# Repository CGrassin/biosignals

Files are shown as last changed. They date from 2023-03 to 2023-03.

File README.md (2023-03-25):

# BioSignals

**This project is work-in-progress.**

BioSignals is a multi-channel, up to 24-bits resolution acquisition system for bio-potentials (EMG, ECG, EEG and more). 

Repository structure:
* **Firmware_BioSignals**: the firmware to be programmed on the board with STM32duino.
* **Electronics_BioSignals**: the circuit board files.
* **Software_BioSignals**: software for the host computer
* **CAD_BioSignals**: 3D files (EEG headware).
* **Interface.md**: description of the data and command interface to the board.

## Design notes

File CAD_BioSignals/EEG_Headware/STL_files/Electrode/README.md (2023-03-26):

# Electrodes holders

Forked from the Ultracortex "Mark III Nova REVISED" repository: https://github.com/OpenBCI/Ultracortex/tree/master/Mark_III_Nova_REVISED

## Print Settings

* Material: PLA
* Supports: NO
* Raft: NO
* Infill: 20%
* Layer Height: 0.2mm
* Number of Shells: 3
* Speed while extruding: 50-70% (slow it down if possible; these parts are detailed)

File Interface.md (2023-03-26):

# Data and command interface

Forked from https://github.com/OpenBCI/Documentation

## Data format

BioSignals sends 33 bytes long packets, following the OpenBCI Cyton data output format.

Each packet contains a header followed by a sample counter, followed by 8 ADS channel data, followed by the three axes values of the accelerometer, followed by a footer. The accelerometer data are optional, and don't need to be sent with every packet when used. if unused, the bytes will read 0. This allows for user defined auxiliary data to be sent in the last six bytes before the footer. Also, there may be room for compressing more samples. Here are details on the format.

**Header**

-   Byte 1: 0xA0  
-   Byte 2: Sample Number

**EEG Data**  
Note: values are 24-bit signed, MSB first

-   Bytes 3-5: Data value for EEG channel 1  
-   Bytes 6-8: Data value for EEG channel 2  
-   Bytes 9-11: Data value for EEG channel 3  
-   Bytes 12-14: Data value for EEG channel 4  
-   Bytes 15-17: Data value for EEG channel 5  
-   Bytes 18-20: Data value for EEG channel 6  
-   Bytes 21-23: Data value for EEG channel 6  
-   Bytes 24-26: Data value for EEG channel 8  

**Aux Data**

-   Bytes 27-32: 6 bytes of data defined and parsed based on the **Footer** below

**Footer**  

-   Byte 33: 0xCX where X is 0-F in hex

The following table is sorted by `Stop Byte`. Drivers should use the `Stop Byte` to determine how to parse the 6 `AUX` bytes.

| Byte 27 | Byte 28 | Byte 29 | Byte 30 | Byte 31 | Byte 32 | Stop Byte | Name                                |
| :-----: | :-----: | :-----: | :-----: | :-----: | :-----: | :-------: | ----------------------------------- |
|   AX1   |   AX0   |   AY1   |   AY0   |   AZ1   |   AZ0   |    0xC0   | Standard with accel                 |
|   UDF   |   UDF   |   UDF   |   UDF   |   UDF   |   UDF   |    0xC1   | Standard with raw aux               |
|   UDF   |   UDF   |   UDF   |   UDF   |   UDF   |   UDF   |    0xC2   | User defined                        |
|    AC   |    AV   |    T3   |    T2   |    T1   |    T0   |    0xC3   | Time stamped **_set_** with accel   |
|    AC   |    AV   |    T3   |    T2   |    T1   |    T0   |    0xC4   | Time stamped with accel             |
|   UDF   |   UDF   |    T3   |    T2   |    T1   |    T0   |    0xC5   | Time stamped **_set_** with raw aux |
|   UDF   |   UDF   |    T3   |    T2   |    T1   |    T0   |    0xC6   | Time stamped with raw aux           |

### 24-Bit Signed Data Values conversion

For the EEG data values, you will note that we are transferring the data as a 24-bit signed integer, which is a bit unusual. We are using this number format because it is the native format used by the ADS129x chip that is at the core of the BioSignals board. To convert this unusual number format into a more standard 32-bit signed integer, you can use the following snippet (Java):

```java

int interpret24bitAsInt32(byte[] byteArray) {     
    int newInt = (  
     ((0xFF & byteArray[0]) <! 16) |  
     ((0xFF & byteArray[1]) <! 8) |   
     (0xFF & byteArray[2])  
    );  
    if ((newInt & 0x00800000) > 0) {  
      newInt |= 0xFF000000;  
    } else {  
      newInt &= 0x00FFFFFF;  
    }  
    return newInt;  
}  

```

## Command interface

On startup, the board sends the following text over the radio:

```

OpenBCI V3 8-16 channel
ADS1299 Device ID: 0xXX
LIS3DH Device ID: 0xXX
Firmware: vX.X.X
$$$

```

### Turn Channels OFF

**1 2 3 4 5 6 7 8**  
These ASCII characters turn the respective channels [1-8] off. The channel will read 0.00 when off during streamData mode. These commands work in and out of streamData mode.

**returns** none, there is no confirmation.

### Turn Channels ON

**! @ # $ % ^ &  \***  
These ASCII characters turn the respective channels [1-8] on. The channel will read ADC output values during streamData mode. These commands work in and out of streamData mode.

**returns** none, there is no confirmation.

### Test Signal Control Commands

**0 - = p [ ]**  
Turn **all** available channels on, and connect them to internal test signal. These are useful for self test and calibration. For example, you can measure the internal noise by sending **0** which connects all inputs to an internal GND. If streaming, the stream will be stopped, the proper registers set on the ADS1x9x, and the stream will be resumed.

-   **0**  Connect to internal GND (VDD - VSS)  
-   **-**  Connect to test signal 1xAmplitude, slow pulse  
-   **=**  Connect to test signal 1xAmplitude, fast pulse  
-   **p**  Connect to DC signal  
-   **\[**  Connect to test signal 2xAmplitude, slow pulse  
-   **]**  Connect to test signal 2xAmplitude, fast pulse  

**Note: Not all possible internal test connections are implemented here.**

**returns** If not streaming, returns `Success: Configured internal test signal.$$$`, if streaming, there is no confirmation.

### Channel Setting Commands

** x (CHANNEL, POWER_DOWN, GAIN_SET, INPUT_TYPE_SET, BIAS_SET, SRB2_SET, SRB1_SET) X **  
Channel Settings commands have six parameters for each ADS channel. To access Channel Settings, first send **x**. The OpenBCI board will then expect the next 7 bytes to be channel settings specific commands. The first byte is the channel number. (If you have the Daisy Module, you can select up to 16 channels to set). The following six ASCII characters are accepted as parameters to set. Lastly, sending **X** will latch the settings to the ADS channel.

**CHANNEL**

-   **1 2 3 4 5 6 7 8**  for single board channel select
-   **Q W E R T Y U I**  for selecting channels on the Daisy Module

**POWER_DOWN**

-   0 = ON (default)
-   1 = OFF    

**GAIN_SET**

-   0 = Gain 1
-   1 = Gain 2
-   2 = Gain 4
-   3 = Gain 6
-   4 = Gain 8
-   5 = Gain 12
-   6 = Gain 24	(default)

**INPUT_TYPE_SET**  
Select the ADC channel input source  

-   0        ADSINPUT_NORMAL     	(default)  
-   1        ADSINPUT_SHORTED          
-   2        ADSINPUT_BIAS_MEAS  
-   3        ADSINPUT_MVDD  
-   4        ADSINPUT_TEMP  
-   5        ADSINPUT_TESTSIG  
-   6        ADSINPUT_BIAS_DRP  
-   7        ADSINPUT_BIAS_DRN  

**BIAS_SET**  
Select to include the channel input in BIAS generation.

-   0 = Remove form BIAS
-   1 = Include in BIAS  (default)  

**SRB2_SET**  
Select to connect this channel's P input to the SRB2 pin. This closes a switch between P input and SRB2 for the given channel, and allows the P input also remain connected to the ADC.  

-   0 = Disconnect this input from SRB2
-   1 = Connect this input to SRB2  (default)  

**SRB1_SET**  
Select to connect all channels' N inputs to SRB1. This effects all pins, and disconnects all N inputs from the ADC.  

-   0 = Disconnect all N inputs from SRB1 (default)
-   1 = Connect all N inputs to SRB1  

**EXAMPLE**

User sends **x  3  0  2  0  0  0  0  X**

'x' enters Channel Settings mode. Channel 3 is set up to be powered up, with gain of 2, normal input, removed from BIAS generation, removed from SRB2, removed from SRB1. The final 'X' latches the settings to the ADS1x9x channel settings register.

You may stack multiple channel settings together such as:

**EXAMPLE**

User sends **x1020000Xx2020000Xx3020000X**

This will set the first three channels.

**returns**

On success:

-   If streaming, no confirmation of success. Note: WiFi Shields will always get a response, even if streaming.
-   If not streaming, returns `Success: Channel set for 3$$$`, where 3 is the channel that was requested to be set.

On failure:

-   If not streaming, NOTE: WiFi shield always sends the following responses without `$$$`
    -   Not enough characters received, `Failure: too few chars$$$` (**example** user sends x102000X)
    -   9th character is not the upper case 'X', `Failure: 9th char not X$$$` (**example** user sends x1020000V)
    -   Too many characters or some other issue, `Failure: Err: too many chars$$$`
-   If not all commands are not received within 1 second, `Timeout processing multi byte message - please send all commands at once as of v2$$$`

**Note: 24&times; gain, SRB1_SET and SRB2_SET are only supported by the ADS1299.**

### Default Channel Settings

**d** To set all channels to default  

**returns** if not streaming, `updating channel settings to default$$$`

**D** To get a report of the default settings send.

**returns** When you query the default settings, expect to get 6 ASCII characters followed by **$$$**

<!-- _Note: Users can change the default channel settings in the initialization function inside the OpenBCI library. Requires re-programming the board._ -->

### LeadOff Impedance Commands

**z (CHANNEL, PCHAN, NCHAN) Z**  
This works similar to the Channel Settings commands. For firmware `v0` and `v1` care must be taken to delay between sending characters, as of `v2.0.0`, you may send as fast as possible in a byte stream. Impedance settings have two parameters for each ADS channel. Impedance is measurable by applying a small 31.5Hz AC signal to the given channel.

-   0 = Test Signal Not Applied (default)
-   1 = Test Signal Applied  

**EXAMPLE**

User sends **z  4  1  0  Z** or `z410Z`

'z' enters Impedance Settings mode. Channel 4 is set up to measure impedance on the P input. The final 'Z' latches the settings to the ADS registers.

**returns**

On success:

-   If streaming, no confirmation of success. Note: WiFi Shields will always get a response, even if streaming.
-   If not streaming, returns `Success: Lead off set for 4$$$`, where 4 is the channel that was requested to be set.

On failure:

-   If not streaming, NOTE: WiFi shield always sends the following responses without `$$$`
    -   Not enough characters received, `Failure: too few chars$$$` (**example** user sends x102000X)
    -   5th character is not the upper case 'X', `Failure: 5th char not Z$$$` (**example** user sends x1020000V)
    -   Too many characters or some other issue, `Failure: Err: too many chars$$$`
-   If not all commands are not received within 1 second, `Timeout processing multi byte message - please send all commands at once as of v2$$$`

<!-- ### SD card Commands

**A S F G H J K L**  
Send to initiate SD card data logging for specified time  

-   A    =      5MIN  
-   S    =      15MIN  
-   F    =      30MIN  
-   G    =      1HR  
-   H    =      2HR  
-   J    =      4HR  
-   K    =      12HR  
-   L    =      24HR  
-   a	   =      about 14 seconds for testing

**j**  
Stop logging data and close SD file   -->

### Stream Data Commands

**b**  
Start streaming data

**returns** none, there is no confirmation. 

<!-- NOTE: when command from WiFi shield, confirmation is `Stream started`. -->

**s**  
Stop Streaming data  

**returns** none, there is no confirmation. 

<!-- NOTE: when command from WiFi shield, confirmation is `Stream stopped`. -->

### Miscellaneous

**?**  
Query register settings  

**returns** Read and report all register settings for the ADS1x9x ~and the LIS3DH~. Expect to get a verbose serial output from the OpenBCI Board, followed by **$$$**  

**v**

Soft reset for the Board peripherals.

### Sample Rate

**~(COMMAND)**  
This works similar to the Channel Settings commands, however, there is no latching character. Power cycling the OpenBCI board will cause the sample rate to reset back to default of 250Hz.

**COMMAND**

-   0 = 16000 Hz
-   1 = 8000 Hz
-   2 = 4000 Hz
-   3 = 2000 Hz
-   4 = 1000 Hz
-   5 = 500 Hz
-   6 = 250 Hz
-   7 = 125 Hz *(not supported by OpenBCI, BioSignals-specific)*
-   ~ = Get current sample rate

**EXAMPLE**

First, user sends **\~~**

**returns** `Sample rate is 250Hz$$$`

Then, user sends **~5**

**returns** `Sample rate set to 500Hz$$$`

NOTE: if not all commands are not received within 1 second, `Timeout processing multi byte message - please send all commands at once as of v2$$$`

### Get Version

**V** To get firmware version

**returns** `v3.1.1$$$`

## Unused ASCII Characters

These are currently unused (and user available) characters in the OpenBCI platform:

**9 ( ) \_ o O f g h k l ' " n N M , . (space)**

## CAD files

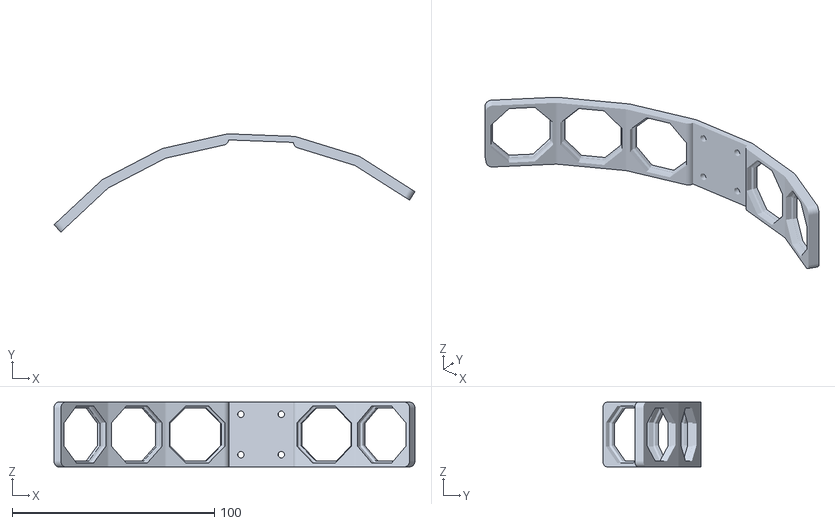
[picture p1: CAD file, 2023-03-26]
CAD_BioSignals/EEG_Headware/STL_files/EEG_band_side.STL
178.6 x 48.6 x 32.0

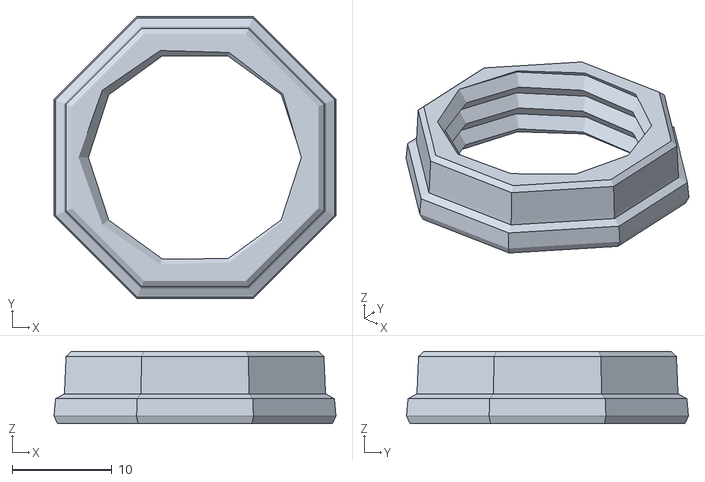
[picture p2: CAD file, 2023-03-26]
CAD_BioSignals/EEG_Headware/STL_files/Electrode/OCTANUT/OCTANUT-LOOSE.stl
28.3 x 28.3 x 7.26

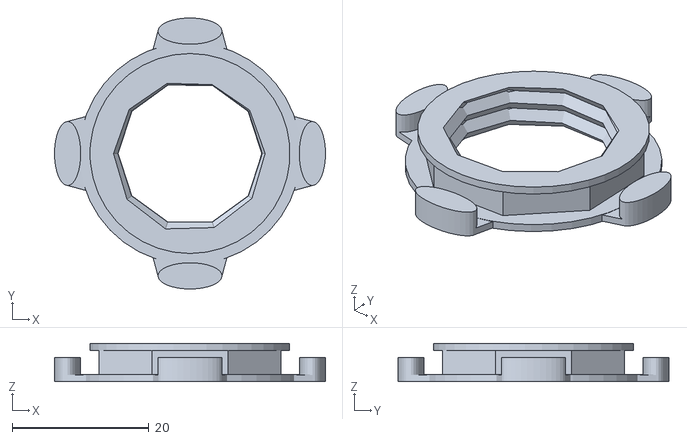
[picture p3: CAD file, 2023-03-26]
CAD_BioSignals/EEG_Headware/STL_files/Electrode/OCTARING.stl
39.7 x 39.7 x 5.59

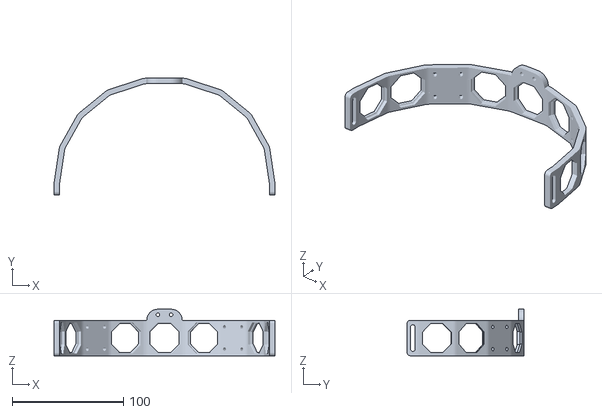
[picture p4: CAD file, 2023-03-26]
CAD_BioSignals/EEG_Headware/STL_files/EEG_band.STL
199.1 x 105.2 x 42.0

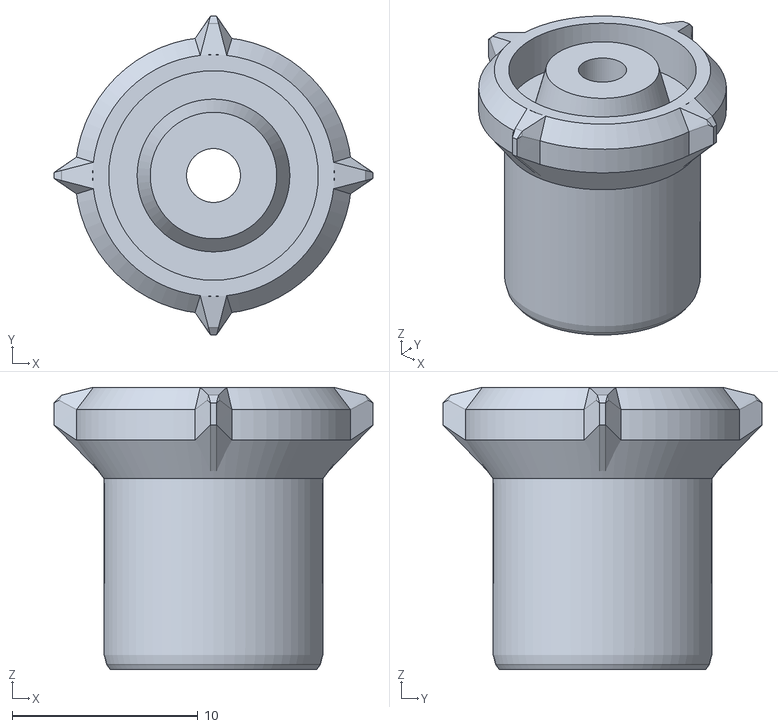
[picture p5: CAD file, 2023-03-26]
CAD_BioSignals/EEG_Headware/STL_files/Electrode/E_HOLDER.stl
17.2 x 17.2 x 15.2

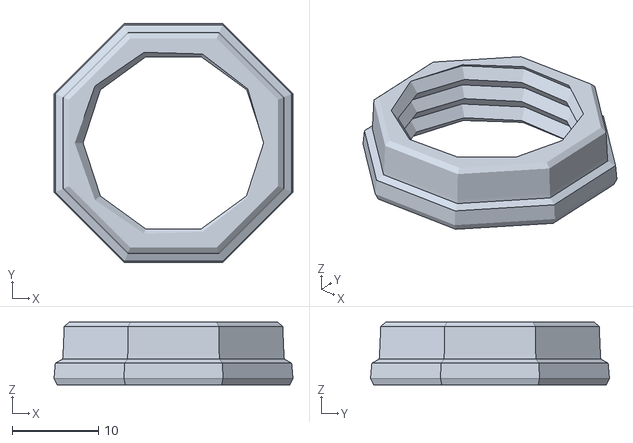
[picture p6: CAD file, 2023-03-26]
CAD_BioSignals/EEG_Headware/STL_files/Electrode/OCTANUT/OCTANUT-TIGHT.stl
27.7 x 27.7 x 7.26

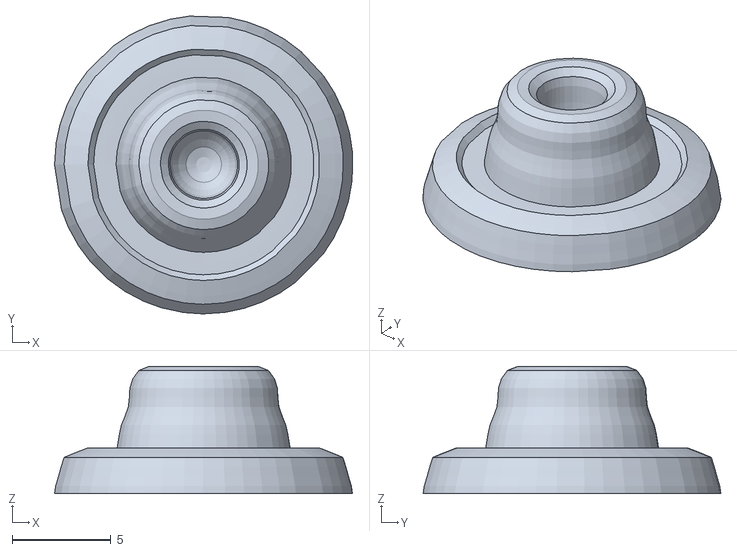
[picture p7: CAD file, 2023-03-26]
CAD_BioSignals/EEG_Headware/STL_files/Electrode/Comfy_Insert.stl
15.1 x 15.1 x 6.43

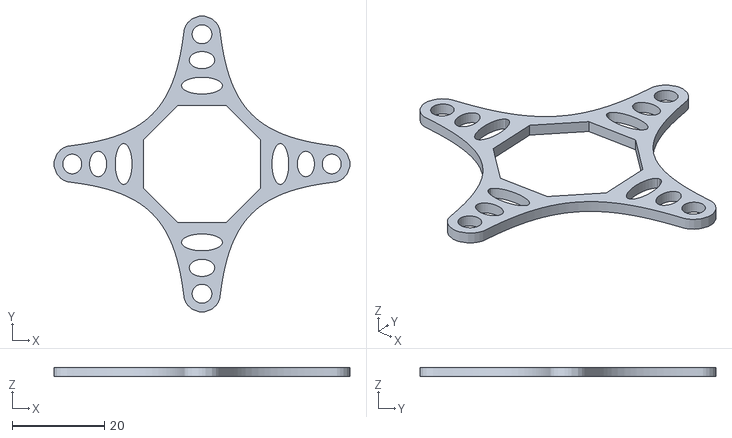
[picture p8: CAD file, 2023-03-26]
CAD_BioSignals/EEG_Headware/STL_files/Electrode/QUADSTAR.stl
64.3 x 64.3 x 2.01

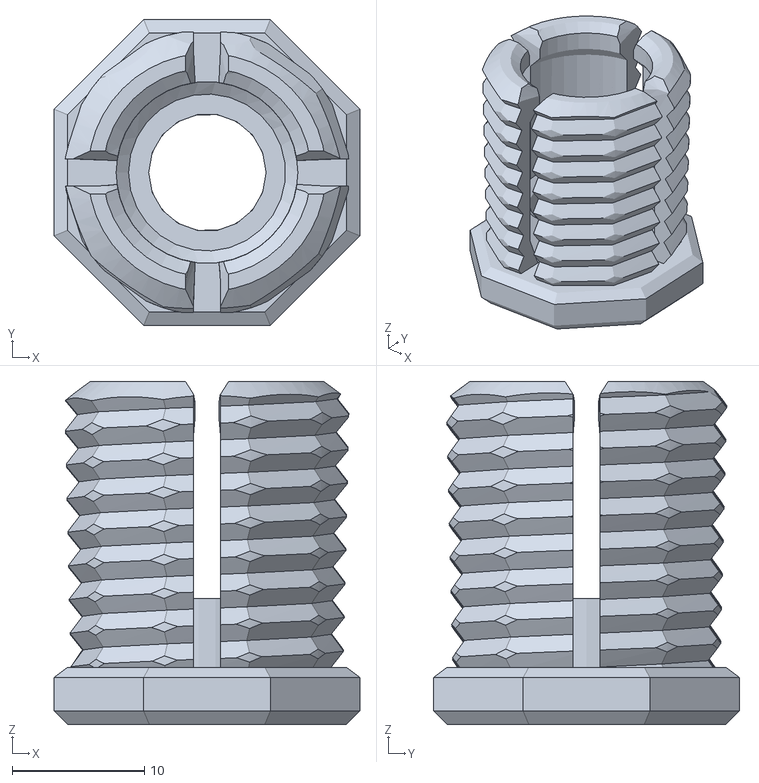
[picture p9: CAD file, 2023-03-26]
CAD_BioSignals/EEG_Headware/STL_files/Electrode/OCTABOLT_20.stl
23.1 x 23.1 x 25.9

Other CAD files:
CAD_BioSignals/EEG_Headware/STL_files/Electrode/OCTANUT/OCTANUT-NORMAL.stl

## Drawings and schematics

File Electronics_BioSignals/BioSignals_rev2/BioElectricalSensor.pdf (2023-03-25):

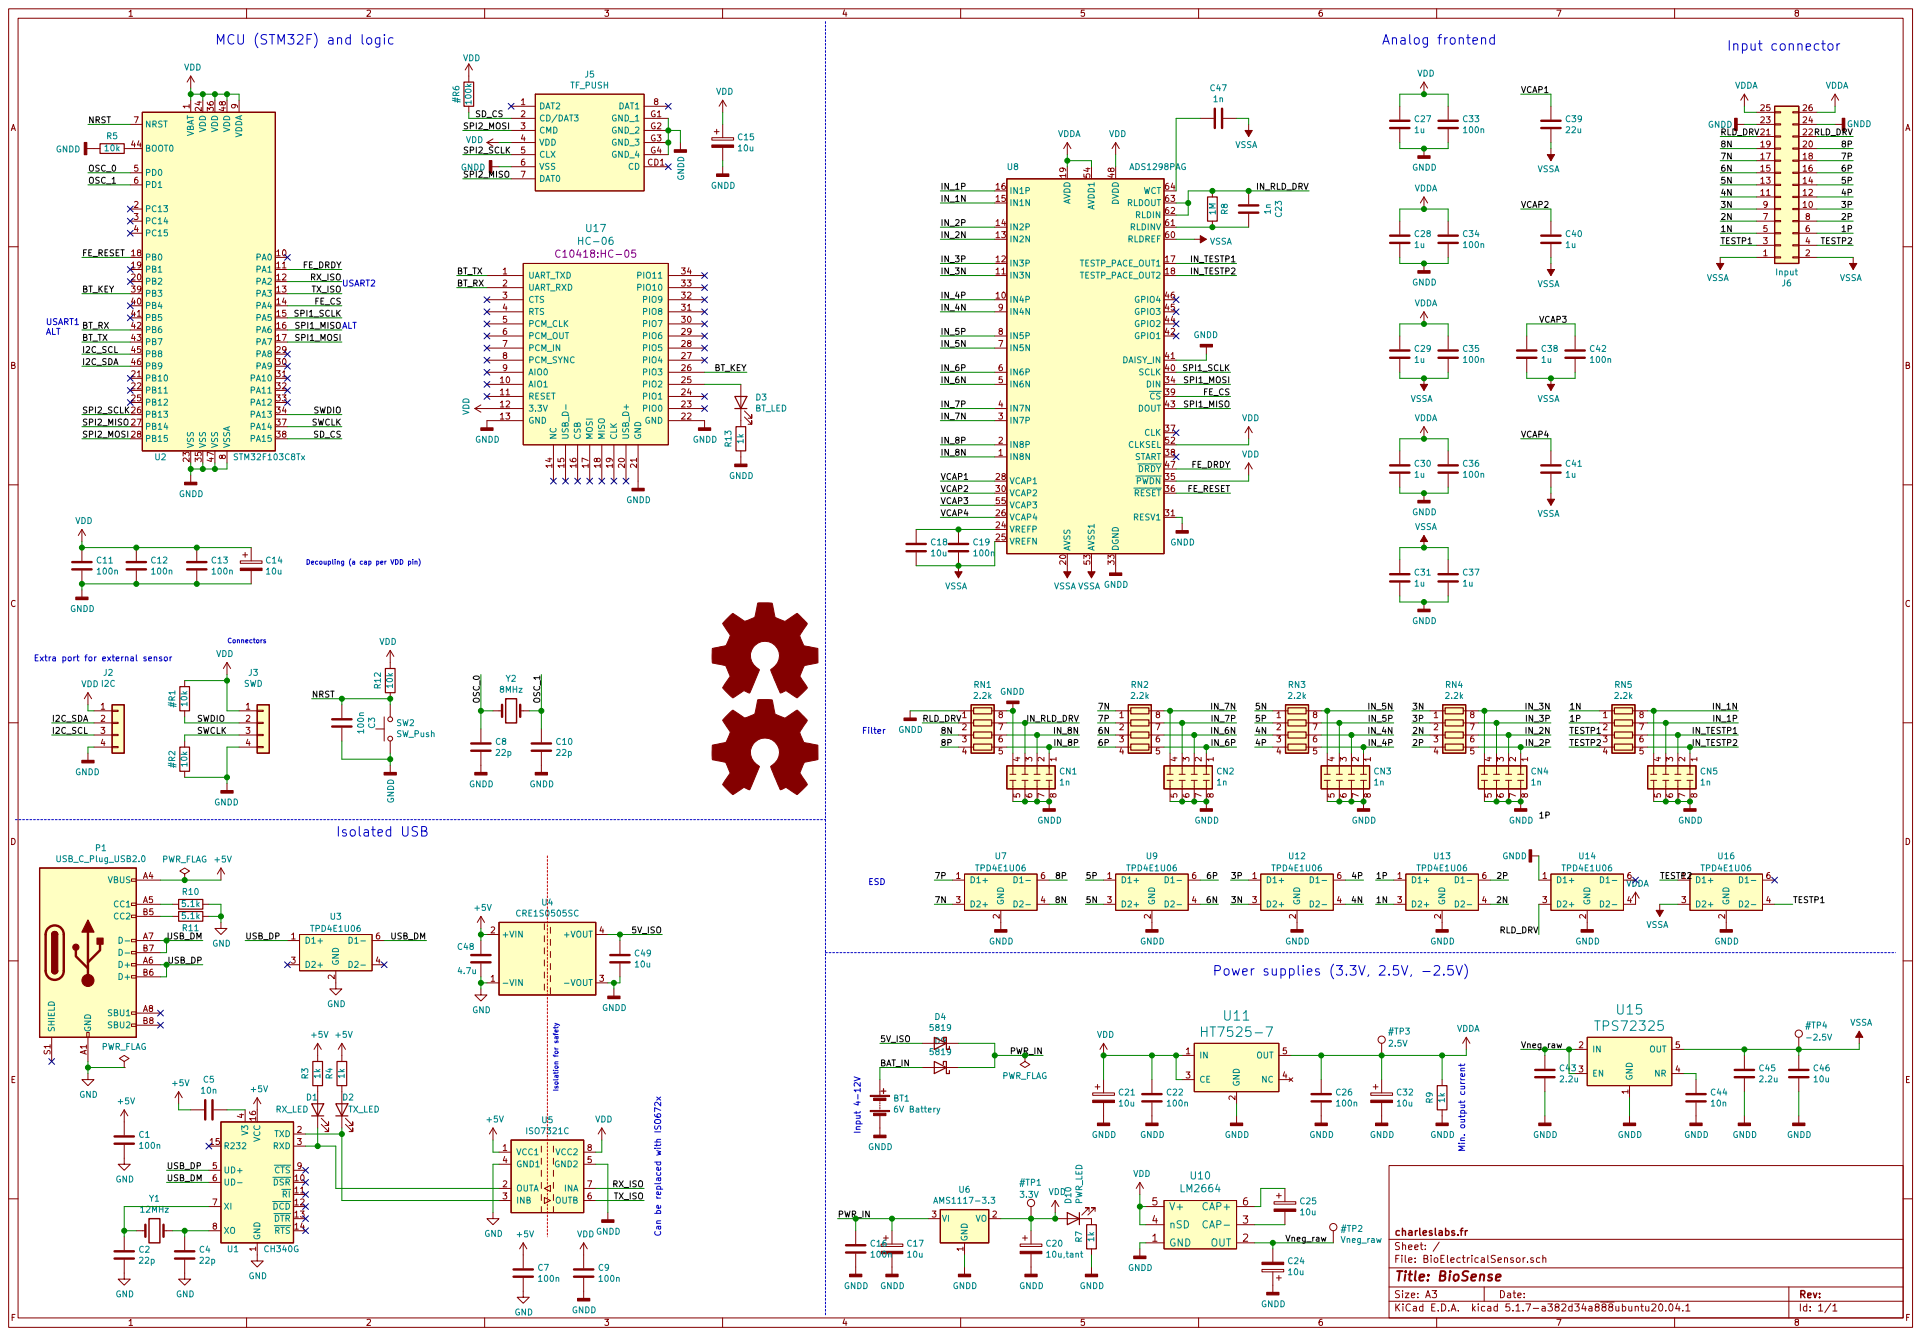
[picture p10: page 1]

Input connector MCU (STM32F) and logic

1 VDD 24 VDD 36 VDD 48 VDDA

9 VSS 23 VSS 35 VSS 47 VSSA U2 8STM32F103C8Tx PWR_FLAG

USART2 Connectors Extra port for external sensor

File: BioElectricalSensor.sch Sheet: / charleslabs.fr C32

1 DSR 10 RI 11 DCD 12 DTR 13 RTS 14 R232 15 VCC 16 TXD 2 RXD 3 V3

4 UD+ 5 UD- 6 XI 7 XO 8 CTS 9 U1 CH340G

1 VO 2 VI 3 U6 AMS1117-3.3 VDD GNDD GND 1 OUT 2 CAP- 3

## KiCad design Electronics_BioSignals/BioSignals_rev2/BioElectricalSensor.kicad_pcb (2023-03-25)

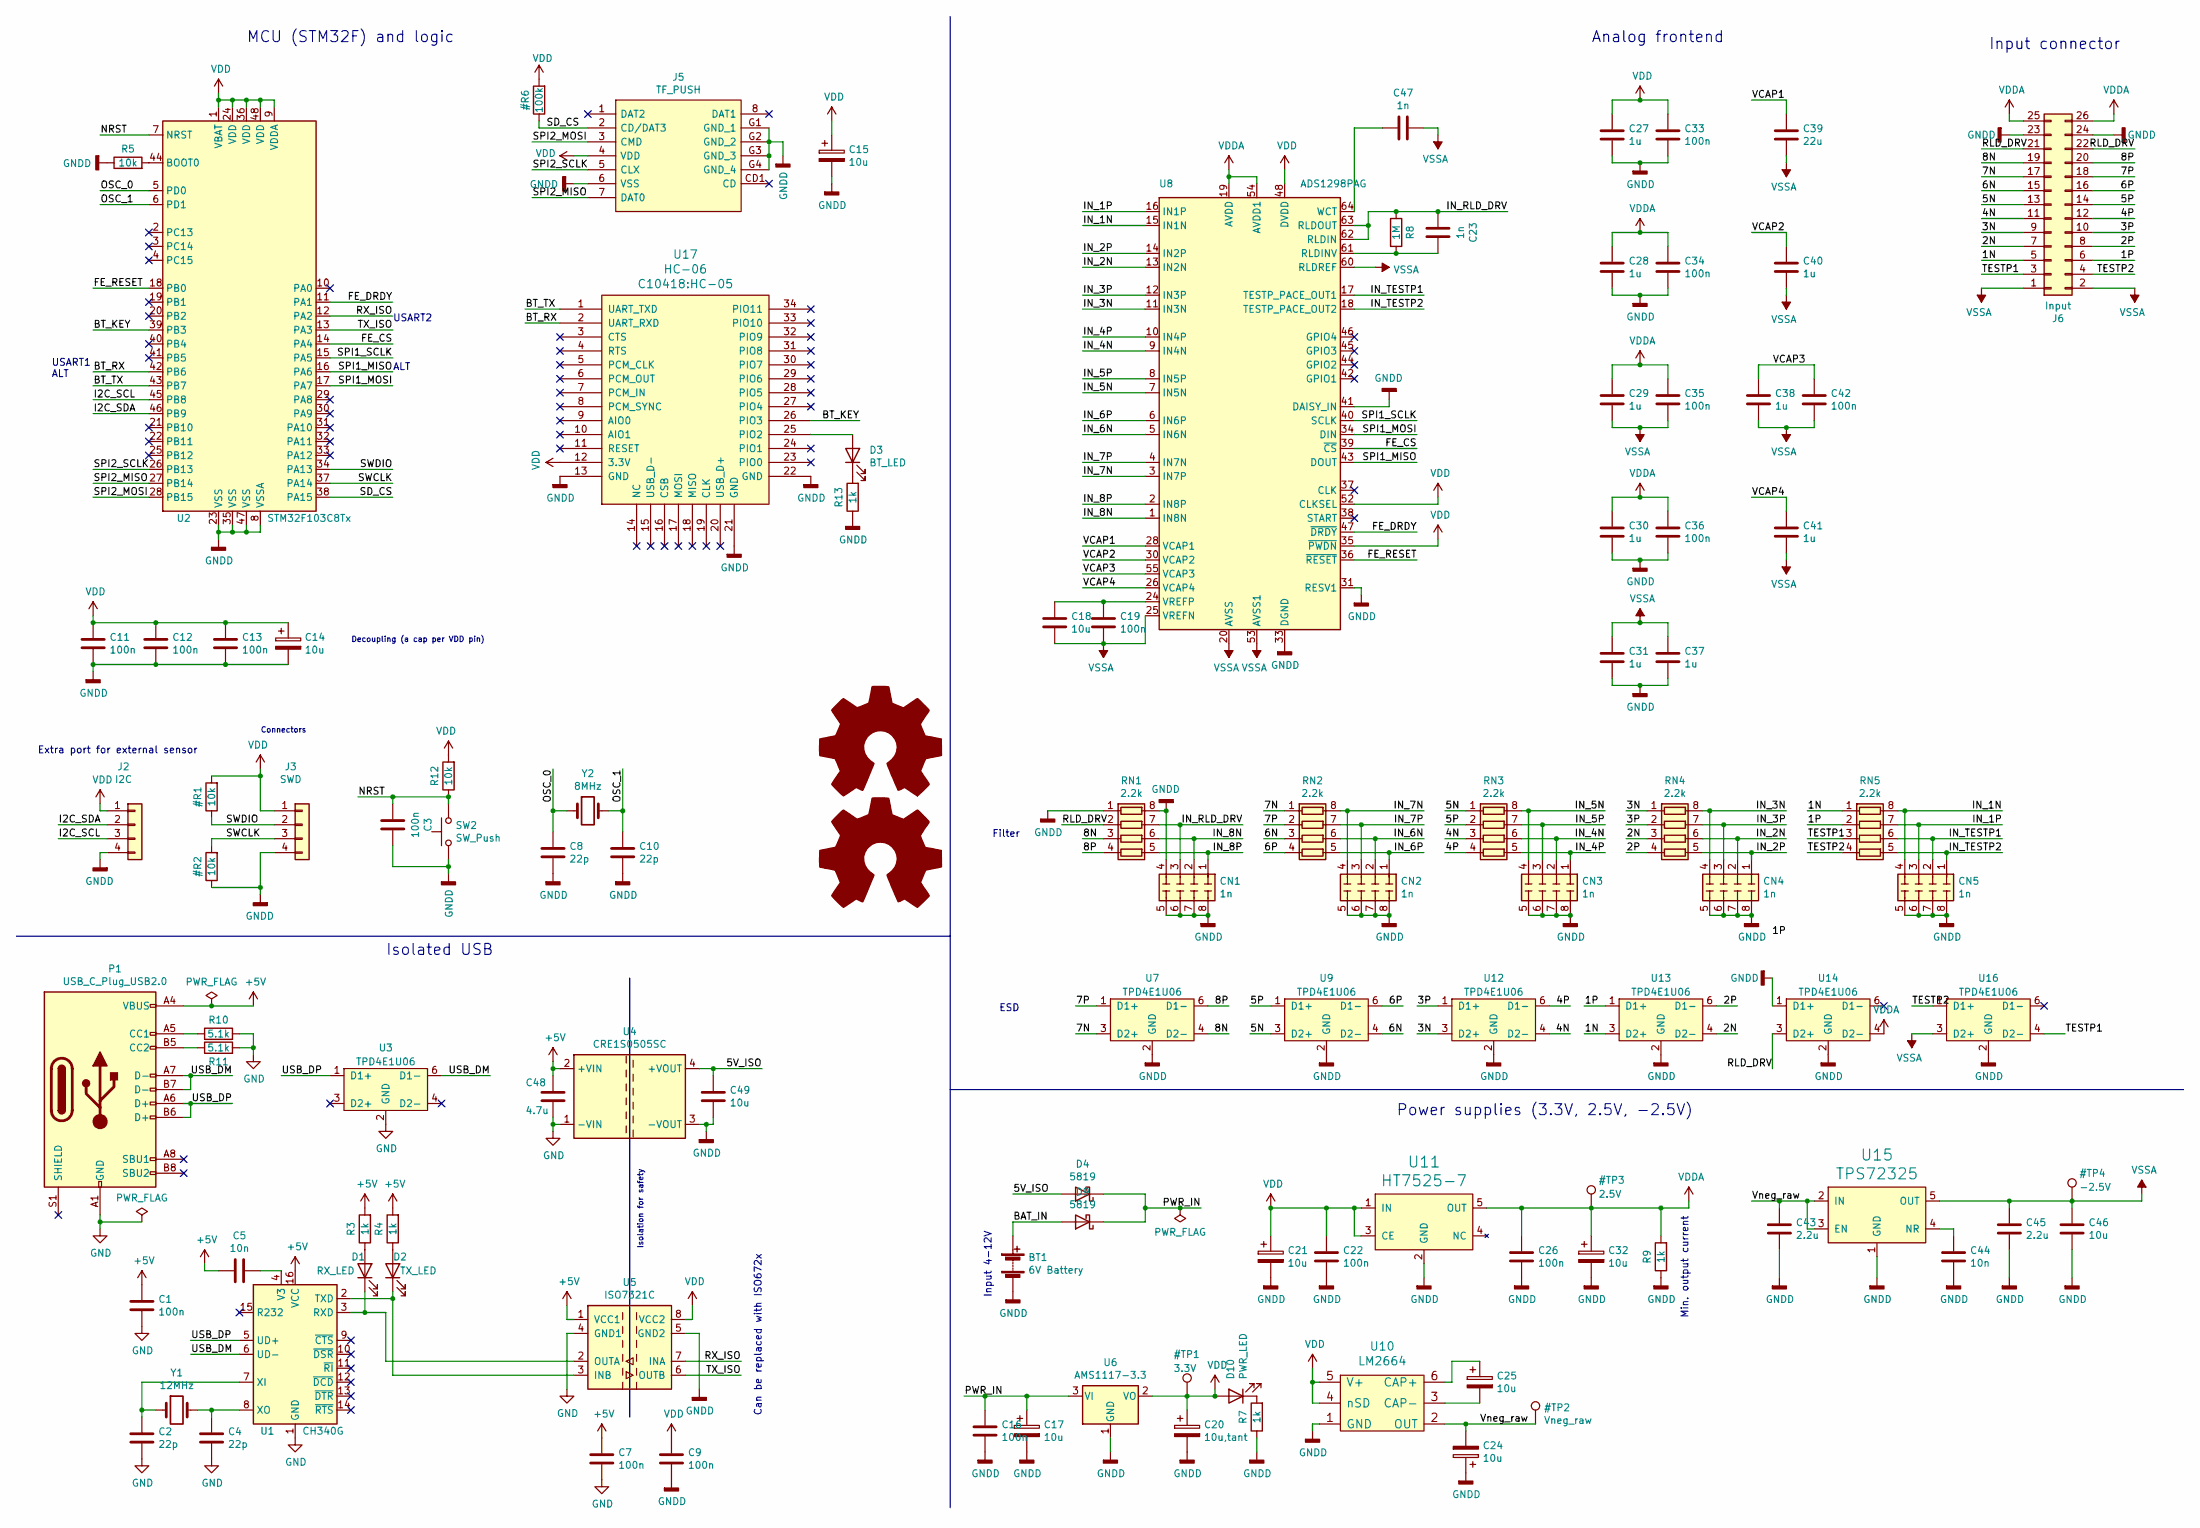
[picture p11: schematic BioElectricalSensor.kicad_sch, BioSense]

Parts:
BT1: 6V Battery; JST_XH_S2B-XH-A-1_1x02_P2.50mm_Horizontal
C1, C3, C7, C9, C11, C12, C13, C16, C19, C22, C26, C33, C34, C35, C36, C42: 100n; C_0805_2012Metric; LCSC C476766
C2, C4, C8, C10: 22p; C_0805_2012Metric; LCSC C24658
C5, C44: 10n; C_0805_2012Metric; LCSC C52278
C14, C17, C18, C21, C24, C25, C32, C46, C49: 10u; C_0805_2012Metric; LCSC C40894
C15: 10u; CP_Elec_5x5.4; LCSC C99837
C20: 10u,tant; CP_EIA-3216-10_Kemet-I; LCSC C110055
C23, C47: 1n; C_0805_2012Metric; LCSC C277515
C27, C28, C29, C30, C31, C37, C38, C40, C41: 1u; C_0805_2012Metric; LCSC C28323
C39: 22u; C_0805_2012Metric; LCSC C129302
C43, C45: 2.2u; C_0805_2012Metric; LCSC C87994
C48: 4.7u; C_0805_2012Metric; LCSC C1779
CN1, CN2, CN3, CN4, CN5: 1n; R_Array_Convex_4x0603; LCSC C507409
D1: RX_LED; LED_0805_2012Metric; LCSC C72037
D2: TX_LED; LED_0805_2012Metric; LCSC C72037
D3: BT_LED; LED_0805_2012Metric; LCSC C72037
D4, D9: 5819; D_SOD-123; LCSC C82544
D10: PWR_LED; LED_0805_2012Metric; LCSC C72037
J2: I2C; PinHeader_1x04_P2.54mm_Vertical
J3: SWD; PinHeader_1x04_P2.54mm_Vertical; LCSC C124378
J5: TF_PUSH; TFPUSH; Manufacturer_Part_Number TF PUSH; LCSC C393941
J6: Input; PinHeader_2x13_P2.54mm_Horizontal; LCSC C358714
LOGO1: Logo_Open_Hardware_Large; Charleslabs_Logo_5mm
LOGO2: Logo_Open_Hardware_Large; Charleslabs_Logo_10mm
P1: USB_C_Plug_USB2.0; USB_C_Receptacle_HRO_TYPE-C-31-M-12; LCSC C393939
R3, R4, R7, R9, R13: 1k; R_0805_2012Metric; LCSC C17513
R5, R12: 10k; R_0805_2012Metric; LCSC C38522
R8: 1M; R_0805_2012Metric; LCSC C17514
R10, R11: 5.1k; R_0805_2012Metric; LCSC C115337
RN1, RN2, RN3, RN4, RN5: 2.2k; R_Array_Convex_4x0603; LCSC C12001
SW2: SW_Push; SW_SPST_CK_RS282G05A3
U1: CH340G; SOIC-16_3.9x9.9mm_P1.27mm; LCSC C14267
U2: STM32F103C8Tx; LQFP-48_7x7mm_P0.5mm; LCSC C8734
U3, U7, U9, U12, U13, U14, U16: TPD4E1U06; SOT-23-6; LCSC C124691
U4: CRE1S0505SC; Converter_DCDC_muRata_CRE1xxxxxxSC_THT; LCSC C18424
U5: ISO7321C; SOIC-8_3.9x4.9mm_P1.27mm; LCSC C187919
U6: AMS1117-3.3; SOT-223-3_TabPin2; LCSC C6186
U8: ADS1298PAG; TQFP-64_10x10mm_P0.5mm
U10: LM2664; SOT-23-6; LCSC C108573
U11: HT7525-7; SOT-23-5; LCSC C259864
U15: TPS72325; SOT-23-5; LCSC C69932
U17: HC-06; HC-05
Y1: 12MHz; Crystal_SMD_5032-2Pin_5.0x3.2mm; LCSC C259045
Y2: 8MHz; Crystal_SMD_5032-2Pin_5.0x3.2mm; LCSC C259040

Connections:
+5V: C1.1, C5.2, C7.1, C48.1, P1.A4 (VBUS), P1.A9 (VBUS), P1.B4 (VBUS), P1.B9 (VBUS), R3.2, R4.2, U1.16 (VCC), U4.2 (+VIN), U5.1 (VCC1)
/1N: J6.5, RN5.1 (R1.1), U13.3 (D2+)
/1P: J6.6, RN5.2 (R2.1), U13.1 (D1+)
/2N: J6.7, RN4.3 (R3.1), U13.4 (D2-)
/2P: J6.8, RN4.4 (R4.1), U13.6 (D1-)
/3N: J6.9, RN4.1 (R1.1), U12.3 (D2+)
/3P: J6.10, RN4.2 (R2.1), U12.1 (D1+)
/4N: J6.11, RN3.3 (R3.1), U12.4 (D2-)
/4P: J6.12, RN3.4 (R4.1), U12.6 (D1-)
/5N: J6.13, RN3.1 (R1.1), U9.3 (D2+)
/5P: J6.14, RN3.2 (R2.1), U9.1 (D1+)
/5V_ISO: C49.1, D4.2 (A), U4.4 (+VOUT)
/6N: J6.15, RN2.3 (R3.1), U9.4 (D2-)
/6P: J6.16, RN2.4 (R4.1), U9.6 (D1-)
/7N: J6.17, RN2.1 (R1.1), U7.3 (D2+)
/7P: J6.18, RN2.2 (R2.1), U7.1 (D1+)
/8N: J6.19, RN1.3 (R3.1), U7.4 (D2-)
/8P: J6.20, RN1.4 (R4.1), U7.6 (D1-)
/BAT_IN: BT1.1 (+), D9.2 (A)
/BT_KEY: U2.39 (PB3), U17.26 (PIO3)
/BT_RX: U2.42 (PB6), U17.2 (UART_RXD)
/BT_TX: U2.43 (PB7), U17.1 (UART_TXD)
/FE_CS: U2.14 (PA4), U8.39 (~CS)
/FE_DRDY: U2.11 (PA1), U8.47 (~DRDY)
/FE_RESET: U2.18 (PB0), U8.36 (~RESET)
/I2C_SCL: J2.3, U2.45 (PB8)
/I2C_SDA: J2.2, U2.46 (PB9)
/IN_1N: CN5.4 (R4.1), RN5.8 (R1.2), U8.15 (IN1N)
/IN_1P: CN5.3 (R3.1), RN5.7 (R2.2), U8.16 (IN1P)
/IN_2N: CN4.2 (R2.1), RN4.6 (R3.2), U8.13 (IN2N)
/IN_2P: CN4.1 (R1.1), RN4.5 (R4.2), U8.14 (IN2P)
/IN_3N: CN4.4 (R4.1), RN4.8 (R1.2), U8.11 (IN3N)
/IN_3P: CN4.3 (R3.1), RN4.7 (R2.2), U8.12 (IN3P)
/IN_4N: CN3.2 (R2.1), RN3.6 (R3.2), U8.9 (IN4N)
/IN_4P: CN3.1 (R1.1), RN3.5 (R4.2), U8.10 (IN4P)
/IN_5N: CN3.4 (R4.1), RN3.8 (R1.2), U8.7 (IN5N)
/IN_5P: CN3.3 (R3.1), RN3.7 (R2.2), U8.8 (IN5P)
/IN_6N: CN2.2 (R2.1), RN2.6 (R3.2), U8.5 (IN6N)
/IN_6P: CN2.1 (R1.1), RN2.5 (R4.2), U8.6 (IN6P)
/IN_7N: CN2.4 (R4.1), RN2.8 (R1.2), U8.3 (IN7P)
/IN_7P: CN2.3 (R3.1), RN2.7 (R2.2), U8.4 (IN7N)
/IN_8N: CN1.2 (R2.1), RN1.6 (R3.2), U8.1 (IN8N)
/IN_8P: CN1.1 (R1.1), RN1.5 (R4.2), U8.2 (IN8P)
/IN_RLD_DRV: C23.2, CN1.3 (R3.1), R8.1, RN1.7 (R2.2), U8.62 (RLDIN), U8.63 (RLDOUT)
/IN_TESTP1: CN5.2 (R2.1), RN5.6 (R3.2), U8.17 (TESTP_PACE_OUT1)
/IN_TESTP2: CN5.1 (R1.1), RN5.5 (R4.2), U8.18 (TESTP_PACE_OUT2)
/NRST: C3.2, R12.1, SW2.2, U2.7 (NRST)
/OSC_0: C8.1, U2.5 (PD0), Y2.1
/OSC_1: C10.1, U2.6 (PD1), Y2.2
/PWR_IN: C16.1, C17.1, D4.1 (K), D9.1 (K), U6.3 (VI)
/RLD_DRV: J6.21, J6.22, RN1.2 (R2.1), U14.3 (D2+)
/RX_ISO: U2.12 (PA2), U5.7 (INA)
/SPI1_MISO: U2.16 (PA6), U8.43 (DOUT)
/SPI1_MOSI: U2.17 (PA7), U8.34 (DIN)
/SPI1_SCLK: U2.15 (PA5), U8.40 (SCLK)
/SPI2_MISO: J5.7 (DAT0), U2.27 (PB14)
/SPI2_MOSI: J5.3 (CMD), U2.28 (PB15)
/SPI2_SCLK: J5.5 (CLX), U2.26 (PB13)
/TESTP1: J6.3, RN5.3 (R3.1), U16.4 (D2-)
/TESTP2: J6.4, RN5.4 (R4.1), U16.1 (D1+)
/TX_ISO: U2.13 (PA3), U5.6 (OUTB)
/USB_DM: P1.A7 (D-), P1.B7 (D-), U1.6 (UD-), U3.6 (D1-)
/USB_DP: P1.A6 (D+), P1.B6 (D+), U1.5 (UD+), U3.1 (D1+)
/VCAP1: C39.1, U8.28 (VCAP1)
/VCAP2: C40.1, U8.30 (VCAP2)
/VCAP3: C38.1, C42.1, U8.55 (VCAP3)
/VCAP4: C41.1, U8.26 (VCAP4)
/Vneg_raw: C24.2, C43.1, U10.2 (OUT), U15.2 (IN), U15.3 (EN)
GND: C1.2, C2.2, C4.2, C7.2, C48.2, P1.A1 (GND), P1.A12 (GND), P1.B1 (GND), P1.B12 (GND), R10.2, R11.2, U1.1 (GND), U3.2 (GND), U4.1 (-VIN), U5.4 (GND1)
unnamed: C2.1, U1.7 (XI), Y1.1
unnamed: C4.1, U1.8 (XO), Y1.2
unnamed: C5.1, U1.4 (V3)
unnamed: C18.1, C19.1, U8.24 (VREFP)
unnamed: C23.1, R8.2, U8.61 (RLDINV)
unnamed: C25.1, U10.6 (CAP+)
unnamed: C25.2, U10.3 (CAP-)
unnamed: C44.1, U15.4 (NR)
unnamed: C47.2, U8.64 (WCT)
unnamed: D1.1 (K), U1.3 (RXD), U5.2 (OUTA)
unnamed: D1.2 (A), R3.1
unnamed: D2.1 (K), U1.2 (TXD), U5.3 (INB)
unnamed: D2.2 (A), R4.1
unnamed: D3.1 (K), R13.2
unnamed: D3.2 (A), U17.25 (PIO2)
unnamed: D10.1 (K), R7.2
unnamed: P1.A5 (CC1), R10.1
unnamed: P1.B5 (CC2), R11.1
unnamed: R5.2, U2.44 (BOOT0)
VDDA: C26.1, C28.1, C29.1, C30.1, C32.1, C34.1, C35.1, C36.1, J6.25, J6.26, R9.2, U8.19 (AVDD), U8.21 (AVDD), U8.22 (AVDD), U8.54 (AVDD1), U8.56 (AVDD), U8.59 (AVDD), U11.5 (OUT), U14.4 (D2-)
VSSA: C18.2, C19.2, C29.2, C31.1, C35.2, C37.1, C38.2, C39.2, C40.2, C41.2, C42.2, C45.1, C46.1, C47.1, J6.1, J6.2, U8.20 (AVSS), U8.23 (AVSS), U8.25 (VREFN), U8.32 (AVSS), U8.53 (AVSS1), U8.57 (AVSS), U8.58 (AVSS), U8.60 (RLDREF), U15.5 (OUT), U16.3 (D2+)

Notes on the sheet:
Power supplies (3.3V, 2.5V, -2.5V)
Decoupling (a cap per VDD pin)
Connectors
ESD
Input connector
USART1 ALT
USART2
ALT
MCU (STM32F) and logic
Min. output current
Analog frontend
Input 4-12V
Can be replaced with ISO672x
Isolation for safety
Filter
Isolated USB
Extra port for external sensor

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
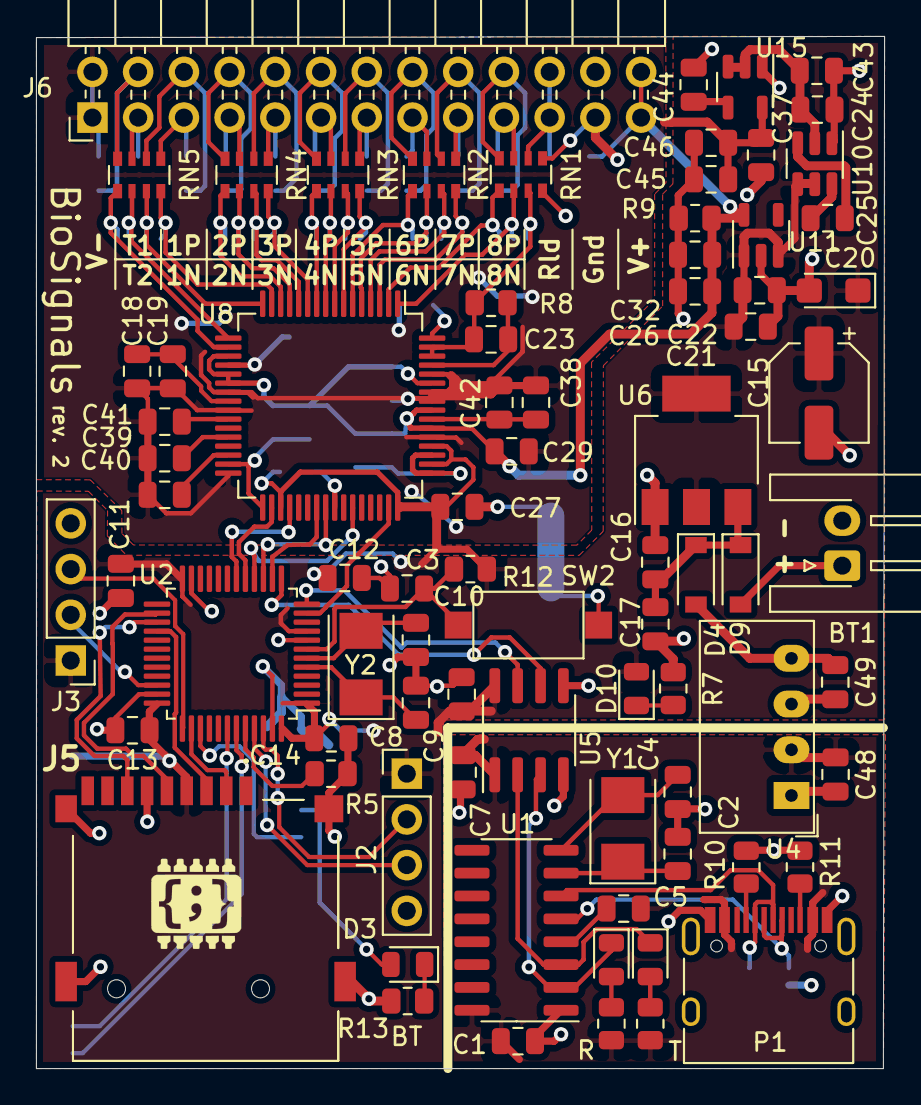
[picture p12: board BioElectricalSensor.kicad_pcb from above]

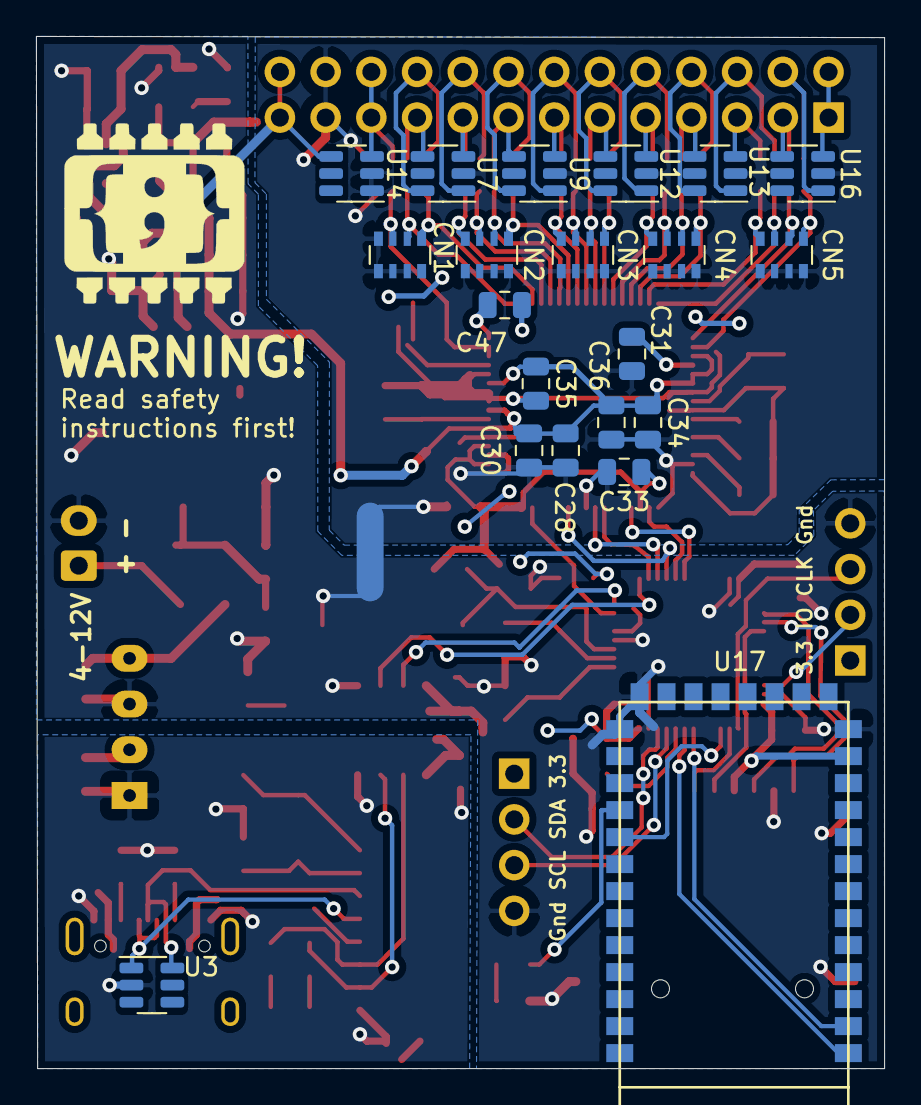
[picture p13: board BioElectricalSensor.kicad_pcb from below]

Board: 2 copper layers, 47.1 x 57.3 mm, 102 parts (22 on the bottom side), 95 nets.

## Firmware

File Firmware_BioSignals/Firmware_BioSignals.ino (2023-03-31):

#include <SPI.h>
#include <SdFat.h>
#include "openbci.h"

// Type of ADC:
// 0 for ADS1194, ADS1196, ADS1198 (UNTESTED).
// 1 for ADS1294, ADS1294R, ADS1296, ADS1296R, ADS1298, ADS1298R.
// 2 for ADS1299, ADS1299-4, ADS1299-6 (UNTESTED).
#define ADS_CHIP_TYPE 1

// Pinout for U2 (STM32F103C8Tx)
#define PIN_FE_DRDY PA1
#define PIN_FE_CS PA4
#define PIN_FE_RESET PB0
#define PIN_SPI1_SCLK PA5
#define PIN_SPI1_MISO PA6
#define PIN_SPI1_MOSI PA7

#define PIN_RX_ISO PA2 /* Connected to CH340 RX (TX on STM32) */
#define PIN_TX_ISO PA3 /* Connected to CH340 TX (RX on STM32) */

#define PIN_SD_CS PA15
#define PIN_SPI2_SCLK PB13
#define PIN_SPI2_MISO PB14
#define PIN_SPI2_MOSI PB15

#define PIN_BT_KEY PB3 /* Unused */
#define PIN_BT_RX PB6 /* Connected to HC-06 RX (TX on STM32) */
#define PIN_BT_TX PB7 /* Connected to HC-06 TX (RX on STM32) */

#define PIN_I2C_SCL PB8 /* Unused */
#define PIN_I2C_SDA PB9 /* Unused */

// TODO
// SD CARD

// CONFIG
//#define SD_CARD_ENABLE
#define SD_CARD_FILENAME "data.csv" // Warning: 8.3 format mandatory TBC
SPIClass SD_SPI2(PIN_SPI2_MOSI,PIN_SPI2_MISO,PIN_SPI2_SCLK);
File sd_file;
#define SD2_CONFIG SdSpiConfig(PIN_SD_CS, DEDICATED_SPI, SD_SCK_MHZ(18), &SD_SPI2)
SdFat SD;

HardwareSerial USB_SERIAL(PIN_TX_ISO, PIN_RX_ISO);
#define USB_SERIAL_SPEED 115200

HardwareSerial BT_SERIAL(PIN_BT_TX, PIN_BT_RX);
#define BT_SERIAL_SPEED 9600

SPIClass SPI1_FE(PIN_SPI1_MOSI,PIN_SPI1_MISO,PIN_SPI1_SCLK);
#if ADS_CHIP_TYPE == 0
  #include "ads119x.h"
  ADS119x ads = ADS119x(PIN_FE_CS, PIN_FE_DRDY, PIN_FE_RESET, &SPI1_FE);
#elif ADS_CHIP_TYPE == 1
  #include "ads129x.h"
  ADS129X ads = ADS129X(PIN_FE_CS, PIN_FE_DRDY, PIN_FE_RESET, &SPI1_FE);
#else
  #include "ads1299.h"
  ADS1299 ads = ADS1299(PIN_FE_CS, PIN_FE_DRDY, PIN_FE_RESET, &SPI1_FE);
#endif
OpenBCI openbci = OpenBCI(&ads, &USB_SERIAL);

void setup() {
  // USB ISO
  USB_SERIAL.begin(USB_SERIAL_SPEED);

  // Bluetooth
  BT_SERIAL.begin(BT_SERIAL_SPEED);

  // SD card (open card and file)
  #ifdef SD_CARD_ENABLE 
    if (SD.begin(SD2_CONFIG)) {
      sd_file = SD.open(SD_CARD_FILENAME, FILE_WRITE);
      if(sd_file){
        sd_file.println("Success!");
        sd_file.close();
        USB_SERIAL.println("Wrote to file");
      }
      else
       USB_SERIAL.println("Failed to create file");
    }
    else
       USB_SERIAL.println("Failed open SD");
  #endif

  // Init the OpenBCI and ADS
  openbci.init();
}

void loop() {
  if(ads.read_data()){
    openbci.sendData(ads.data);
  }
  openbci.readCMD();
}

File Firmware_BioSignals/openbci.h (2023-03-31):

/*
* This class is the OpenBCI interface definition for the board (commands and data output interface).
* Adapted from https://github.com/OpenBCI/OpenBCI_Cyton_Library/blob/master/OpenBCI_32bit_Library_Definitions.h
* Interface documented: https://docs.openbci.com/Cyton/CytonSDK/ and https://docs.openbci.com/Cyton/CytonDataFormat/
*/
#ifndef __OpenBCI_INCLUDE
#define __OpenBCI_INCLUDE

#include "ads1x9x.h"
#include "FIRFilter.h"
#include <Arduino.h>

#define PCKT_START 0xA0  // prefix for data packet error checking
#define MULTI_CHAR_COMMAND_TIMEOUT_MS 1000

// OPENBCI_COMMANDS
/** Turning channels off */
#define OPENBCI_CHANNEL_OFF_1 '1'
#define OPENBCI_CHANNEL_OFF_2 '2'
#define OPENBCI_CHANNEL_OFF_3 '3'
#define OPENBCI_CHANNEL_OFF_4 '4'
#define OPENBCI_CHANNEL_OFF_5 '5'
#define OPENBCI_CHANNEL_OFF_6 '6'
#define OPENBCI_CHANNEL_OFF_7 '7'
#define OPENBCI_CHANNEL_OFF_8 '8'
#define OPENBCI_CHANNEL_OFF_9 'q'
#define OPENBCI_CHANNEL_OFF_10 'w'
#define OPENBCI_CHANNEL_OFF_11 'e'
#define OPENBCI_CHANNEL_OFF_12 'r'
#define OPENBCI_CHANNEL_OFF_13 't'
#define OPENBCI_CHANNEL_OFF_14 'y'
#define OPENBCI_CHANNEL_OFF_15 'u'
#define OPENBCI_CHANNEL_OFF_16 'i'

/** Turn channels on */
#define OPENBCI_CHANNEL_ON_1 '!'
#define OPENBCI_CHANNEL_ON_2 '@'
#define OPENBCI_CHANNEL_ON_3 '#'
#define OPENBCI_CHANNEL_ON_4 '$'
#define OPENBCI_CHANNEL_ON_5 '%'
#define OPENBCI_CHANNEL_ON_6 '^'
#define OPENBCI_CHANNEL_ON_7 '&'
#define OPENBCI_CHANNEL_ON_8 '*'
#define OPENBCI_CHANNEL_ON_9 'Q'
#define OPENBCI_CHANNEL_ON_10 'W'
#define OPENBCI_CHANNEL_ON_11 'E'
#define OPENBCI_CHANNEL_ON_12 'R'
#define OPENBCI_CHANNEL_ON_13 'T'
#define OPENBCI_CHANNEL_ON_14 'Y'
#define OPENBCI_CHANNEL_ON_15 'U'
#define OPENBCI_CHANNEL_ON_16 'I'

/** Test Signal Control Commands
 * 1x - Voltage will be 1 * (VREFP - VREFN) / 2.4 mV
 * 2x - Voltage will be 2 * (VREFP - VREFN) / 2.4 mV
 */
#define OPENBCI_TEST_SIGNAL_CONNECT_TO_DC 'p'
#define OPENBCI_TEST_SIGNAL_CONNECT_TO_GROUND '0'
#define OPENBCI_TEST_SIGNAL_CONNECT_TO_PULSE_1X_FAST '='
#define OPENBCI_TEST_SIGNAL_CONNECT_TO_PULSE_1X_SLOW '-'
#define OPENBCI_TEST_SIGNAL_CONNECT_TO_PULSE_2X_FAST ']'
#define OPENBCI_TEST_SIGNAL_CONNECT_TO_PULSE_2X_SLOW '['

/** Channel Setting Commands */
#define OPENBCI_CHANNEL_CMD_ADC_Normal '0'
#define OPENBCI_CHANNEL_CMD_ADC_Shorted '1'
#define OPENBCI_CHANNEL_CMD_ADC_BiasDRP '6'
#define OPENBCI_CHANNEL_CMD_ADC_BiasDRN '7'
#define OPENBCI_CHANNEL_CMD_ADC_BiasMethod '2'
#define OPENBCI_CHANNEL_CMD_ADC_MVDD '3'
#define OPENBCI_CHANNEL_CMD_ADC_Temp '4'
#define OPENBCI_CHANNEL_CMD_ADC_TestSig '5'
#define OPENBCI_CHANNEL_CMD_BIAS_INCLUDE '1'
#define OPENBCI_CHANNEL_CMD_BIAS_REMOVE '0'
#define OPENBCI_CHANNEL_CMD_CHANNEL_1 '1'
#define OPENBCI_CHANNEL_CMD_CHANNEL_2 '2'
#define OPENBCI_CHANNEL_CMD_CHANNEL_3 '3'
#define OPENBCI_CHANNEL_CMD_CHANNEL_4 '4'
#define OPENBCI_CHANNEL_CMD_CHANNEL_5 '5'
#define OPENBCI_CHANNEL_CMD_CHANNEL_6 '6'
#define OPENBCI_CHANNEL_CMD_CHANNEL_7 '7'
#define OPENBCI_CHANNEL_CMD_CHANNEL_8 '8'
#define OPENBCI_CHANNEL_CMD_CHANNEL_9 'Q'
#define OPENBCI_CHANNEL_CMD_CHANNEL_10 'W'
#define OPENBCI_CHANNEL_CMD_CHANNEL_11 'E'
#define OPENBCI_CHANNEL_CMD_CHANNEL_12 'R'
#define OPENBCI_CHANNEL_CMD_CHANNEL_13 'T'
#define OPENBCI_CHANNEL_CMD_CHANNEL_14 'Y'
#define OPENBCI_CHANNEL_CMD_CHANNEL_15 'U'
#define OPENBCI_CHANNEL_CMD_CHANNEL_16 'I'
#define OPENBCI_CHANNEL_CMD_GAIN_1 '0'
#define OPENBCI_CHANNEL_CMD_GAIN_2 '1'
#define OPENBCI_CHANNEL_CMD_GAIN_4 '2'
#define OPENBCI_CHANNEL_CMD_GAIN_6 '3'
#define OPENBCI_CHANNEL_CMD_GAIN_8 '4'
#define OPENBCI_CHANNEL_CMD_GAIN_12 '5'
#define OPENBCI_CHANNEL_CMD_GAIN_24 '6'
#define OPENBCI_CHANNEL_CMD_LATCH 'X'
#define OPENBCI_CHANNEL_CMD_POWER_OFF '1'
#define OPENBCI_CHANNEL_CMD_POWER_ON '0'
#define OPENBCI_CHANNEL_CMD_SET 'x'
#define OPENBCI_CHANNEL_CMD_SRB1_CONNECT '1'
#define OPENBCI_CHANNEL_CMD_SRB1_DISCONNECT '0'
#define OPENBCI_CHANNEL_CMD_SRB2_CONNECT '1'
#define OPENBCI_CHANNEL_CMD_SRB2_DISCONNECT '0'

/** Default Channel Settings */
#define OPENBCI_CHANNEL_DEFAULT_ALL_SET 'd'
#define OPENBCI_CHANNEL_DEFAULT_ALL_REPORT 'D'

/** LeadOff Impedance Commands */
#define OPENBCI_CHANNEL_IMPEDANCE_LATCH 'Z'
#define OPENBCI_CHANNEL_IMPEDANCE_SET 'z'
#define OPENBCI_CHANNEL_IMPEDANCE_TEST_SIGNAL_APPLIED '1'
#define OPENBCI_CHANNEL_IMPEDANCE_TEST_SIGNAL_APPLIED_NOT '0'

/** SD card Commands */
#define OPENBCI_SD_LOG_FOR_HOUR_1 'G'
#define OPENBCI_SD_LOG_FOR_HOUR_2 'H'
#define OPENBCI_SD_LOG_FOR_HOUR_4 'J'
#define OPENBCI_SD_LOG_FOR_HOUR_12 'K'
#define OPENBCI_SD_LOG_FOR_HOUR_24 'L'
#define OPENBCI_SD_LOG_FOR_MIN_5 'A'
#define OPENBCI_SD_LOG_FOR_MIN_15 'S'
#define OPENBCI_SD_LOG_FOR_MIN_30 'F'
#define OPENBCI_SD_LOG_FOR_SEC_14 'a'
#define OPENBCI_SD_LOG_STOP 'j'

/** Stream Data Commands */
#define OPENBCI_STREAM_START 'b'
#define OPENBCI_STREAM_STOP 's'

/** Miscellaneous */
#define OPENBCI_MISC_QUERY_REGISTER_SETTINGS '?'
#define OPENBCI_MISC_SOFT_RESET 'v'

/** 16 Channel Commands */
#define OPENBCI_CHANNEL_MAX_NUMBER_8 'c'
#define OPENBCI_CHANNEL_MAX_NUMBER_16 'C'

#define OPENBCI_BOARD_MODE_SET '/'

#define OPENBCI_GET_VERSION 'V'

/** Set sample rate */
#define OPENBCI_SAMPLE_RATE_SET '~'

/** Insert marker into the stream */
#define OPENBCI_INSERT_MARKER '`'

/** Sync Clocks */
#define OPENBCI_TIME_SET '<'
#define OPENBCI_TIME_STOP '>'

/** Wifi Stuff */
#define OPENBCI_WIFI_ATTACH '{'
#define OPENBCI_WIFI_REMOVE '}'
#define OPENBCI_WIFI_STATUS ':'
#define OPENBCI_WIFI_RESET ';'

// Custom
#define OPENBCI_BUFFER_LENGTH 10
#define OPENBCI_PACKAGE_STOP_BYTE 0xC2

// Messages
#define OPENBCI_EOT "$$$"
#define OPENBCI_FIRMWARE_VERSION "v3.0.0"
#define OPENBCI_CMD_TIMEOUT_MSG "Timeout processing multi byte message - please send all commands at once as of v2$$$"
#define OPENBCI_CMD_SET_SAMPLERATE_MSG_0 "Sample rate set to "
#define OPENBCI_CMD_GET_SAMPLERATE_MSG_0 "Sample rate is "
#define OPENBCI_CMD_SET_SAMPLERATE_MSG_1 "Hz$$$"
#define OPENBCI_CMD_TESTSIGNAL_SUCCESS_MSG "Success: Configured internal test signal.$$$"
#define OPENBCI_CMD_CHANNEL_DEFAULTS_UPDATE_MSG "updating channel settings to default$$$"
#define OPENBCI_CMD_LOFF_SUCCESS_MSG "Success: Lead off set for "

// Defaults
#define OPENBCI_DEFAULT_SAMPLERATE ADS1X9X::SAMPLE_RATE_250
#define OPENBCI_CHANNEL_DEFAULT_PD false
#define OPENBCI_CHANNEL_DEFAULT_GAIN 12
#define OPENBCI_CHANNEL_DEFAULT_INPUT_TYPE ADS1X9X::INPUT_NORMAL
#define OPENBCI_CHANNEL_DEFAULT_BIAS true
#define OPENBCI_CHANNEL_DEFAULT_SRB2 true
#define OPENBCI_CHANNEL_DEFAULT_SRB1 false
#define OPENBCI_CMD_CHANNEL_DEFAULTS_MSG "050110$$$"

class OpenBCI {
private:
  ADS1X9X* ads;
  HardwareSerial* serial;
  // SdFat *SD;
  unsigned long multiCharCmdTimeout = 0;  // the timeout in millis of the current multi char command
  char cmdBuffer[OPENBCI_BUFFER_LENGTH];
  byte cmdIdx = 0; // Current index in the command buffer
  uint8_t package_counter = 0; // Package counter
  uint8_t sample_counter = 0; // Sample counter
  uint8_t downsampling_factor = 1; // Divides the data rate by this factor (e.g. 500 SPS and setting this to 2 = 250 messages per second)
  ADS1X9X::SAMPLE_RATE current_sample_rate = OPENBCI_DEFAULT_SAMPLERATE;

public:
  /** Constructor for an OpenBCI interface object.
   * @param ads An uninitialized ADS object.
   * @param serial The input/output serial interface.
   */
  OpenBCI(ADS1X9X* ads, HardwareSerial* serial);
  /** Inits the ADS and OpenBCI interface objects. */
  void init();
  /** Sends a 33 bytes OpenBCI packet.
   * @param value A 24 byte register to send.
   */
  void sendData(uint8_t* value);
  /** Reads and processes command (if there is any). */
  void readCMD();

private:
  // Process commands
  void processCMD();
  void processCMDChannelSet();
  void processCMDQuery();
  void processCMDSampleRate();
  void processCMDImpedance();
  void testSignals(uint8_t config2, bool shorted);
  void startUpMessage();
  static bool isSingleCharCmd(char cmd);

  // Helper functions
  void printHex(byte _data);
  uint8_t getChannelFromCommand(char asciiChar);
  const char * getSampleRate();
};
#endif

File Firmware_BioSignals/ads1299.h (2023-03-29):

/*
* This class supports: ADS1299.
*/
#ifndef __ADS1299_INCLUDE
#define __ADS1299_INCLUDE

#include <Arduino.h>
#include <SPI.h>
#include "ads1x9x.h"

// ---------------------
// Register map
#define ADS1299_REG_MISC1 0x15
#define ADS1299_REG_MISC2 0x16
// 0x18 and 0x19 don't exist
// ---------------------
// CONFIG BIT MASKS
// CONFIG 1
#define ADS1299_REG_CONFIG1_RESERVED 0b10010000  /* Reserved bits to set to 1 */
#define ADS1299_REG_CONFIG1_16KSPS 0b00000000
#define ADS1299_REG_CONFIG1_8KSPS 0b00000001
#define ADS1299_REG_CONFIG1_4KSPS 0b00000010
#define ADS1299_REG_CONFIG1_2KSPS 0b00000011
#define ADS1299_REG_CONFIG1_1KSPS 0b00000100
#define ADS1299_REG_CONFIG1_500SPS 0b00000101
#define ADS1299_REG_CONFIG1_250SPS 0b00000110
// CONFIG 2
#define ADS1299_REG_CONFIG2_RESERVED 0b11000000  /* Reserved bits to set to 1 */
// CONFIG 3
#define ADS1299_REG_CONFIG3_RESERVED 0b01100000  /* Reserved bits to set to 1 */
// Individual Channel Settings
#define ADS1299_REG_CHnSET_GAIN_1 0b00000000
#define ADS1299_REG_CHnSET_GAIN_2 0b00010000
#define ADS1299_REG_CHnSET_GAIN_4 0b00100000
#define ADS1299_REG_CHnSET_GAIN_6 0b00110000
#define ADS1299_REG_CHnSET_GAIN_8 0b01000000
#define ADS1299_REG_CHnSET_GAIN_12 0b01010000
#define ADS1299_REG_CHnSET_GAIN_24 0b01100000
#define ADS1299_REG_CHnSET_SRB2    0b00001000
// MISC1
#define ADS1299_REG_MISC1_SRB1    0b00100000
// ---------------------

class ADS1299: public ADS1X9X{
public:
  ADS1299(int cs_pin_set, int drdy_pin_set, int reset_pin_set, SPIClass* spi_set);
  void all_defaults();
  uint8_t set_sample_rate(SAMPLE_RATE sr);
  virtual uint8_t set_channel_settings(uint8_t channelnumber, bool powerdown, uint8_t gain, INPUT_TYPE mux, bool bias, bool srb2, bool srb1);
  const char * getRegisterName(uint8_t _address);
};
#endif

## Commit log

2023-03-25 Added electronics rev1
    [BioElectricalSensor-B_Cu.gbr, BioElectricalSensor-B_Mask.gbr, BioElectricalSensor-B_Paste.gbr, BioElectricalSensor-B_SilkS.gbr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]
2023-03-25 Added electronics rev2
    [BioElectricalSensor-B_Cu.gbr, BioElectricalSensor-B_Mask.gbr, BioElectricalSensor-B_Paste.gbr, BioElectricalSensor-B_SilkS.gbr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]
2023-03-25 Fixed sample rate command ("~")
2023-03-26 Proper support of sample rate implemented in ADS119x, refactoring
2023-03-26 Added CAD files
    [Comfy_Insert.stl, EEG_band.STL, EEG_band_side.STL, E_HOLDER.stl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]
2023-03-27 Better handling channel and sample rate defaults, refactoring
2023-03-31 Added FIR downsampling filter
2023-03-31 Added helper function to convert samples to standard integer
2023-04-05 Fixed FIR filter implementation
